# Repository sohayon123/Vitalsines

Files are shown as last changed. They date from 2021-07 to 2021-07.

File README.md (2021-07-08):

# Vitalsines
 
During my time as a co-op student at Vitalsines, I was responsible for the design and assembly of a variety of mechanical and electrical projects, however, the main project that I worked on was a device with the objective of measuring pulse wave velocity in a comfortable and easy way. 

## PCB Design
I developed 3 different PCBs for this project, one for filtering incoming data from piezo sensors of my design, one for aggregating sensor data lines, and one for sending this data to a DAQ. These PCBs were extremely small, at only 2cm diameter, and were assembled by hand. They contained a adjustable low pass filter to get rid of some of the noise in the analog signal from the piezo. The component size for this PCB was 0603 and the board was designed to have 4 layers, one ground plane and one 10V power plane, to help clean up the traces.

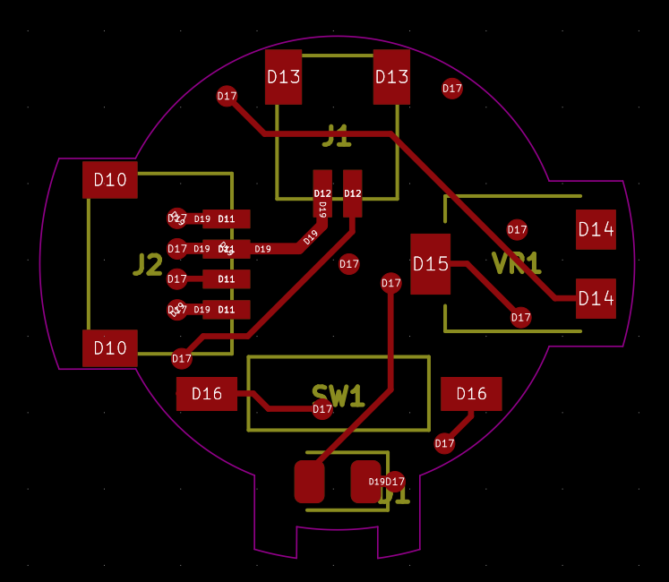
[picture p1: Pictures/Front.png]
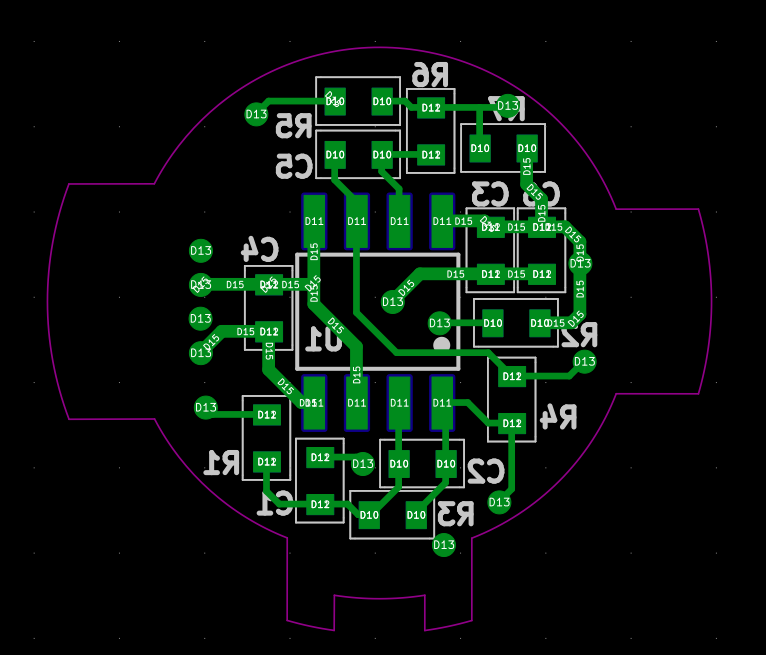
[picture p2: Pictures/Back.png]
  

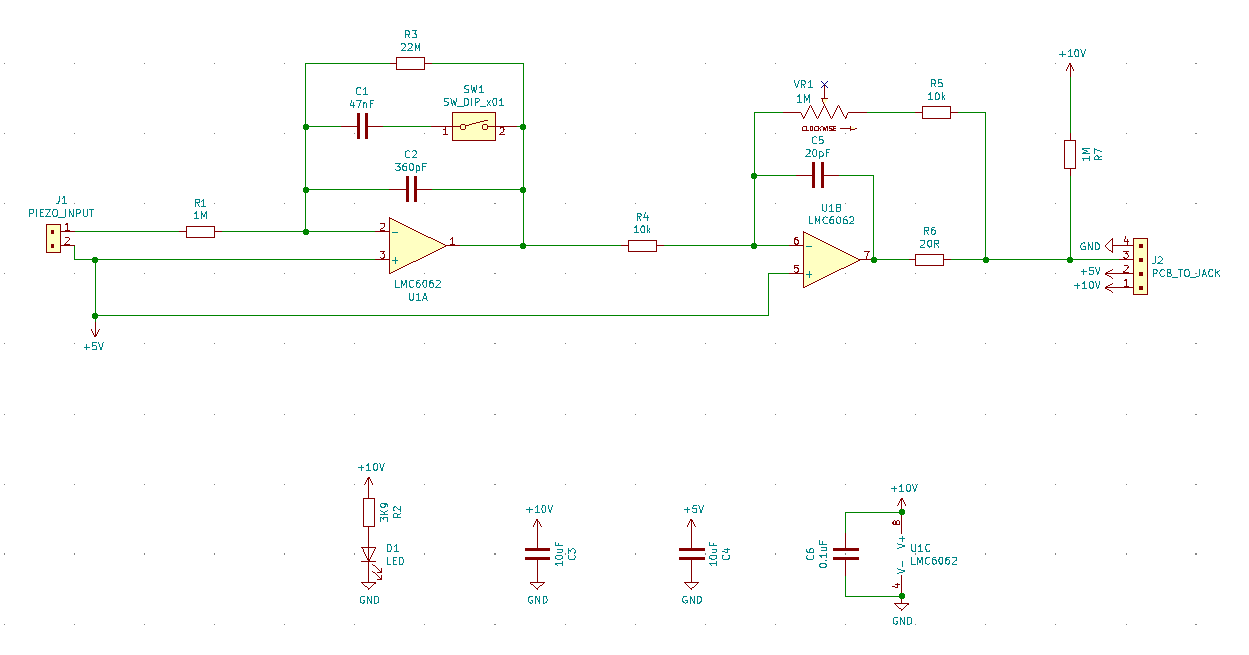
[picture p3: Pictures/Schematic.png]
 

## Mechanical Design

The mechanical design involved creating a strap that would host all of the electronics and sit comfortably on the chest. It also involved the design of some enclosures for the piezo sensors. Below are some pictures of the final result and some of the CAD files. The strap was designed with some areas of varying thickness to allow the PCBs to clip directly into the prototype strap. There were some cavities left in the strap as well to accomodate the various sensor cables.

  

[Link to Cad Viewer!](https://github.com/sohayon123/Vitalsines/blob/main/CAD/strap.STL)

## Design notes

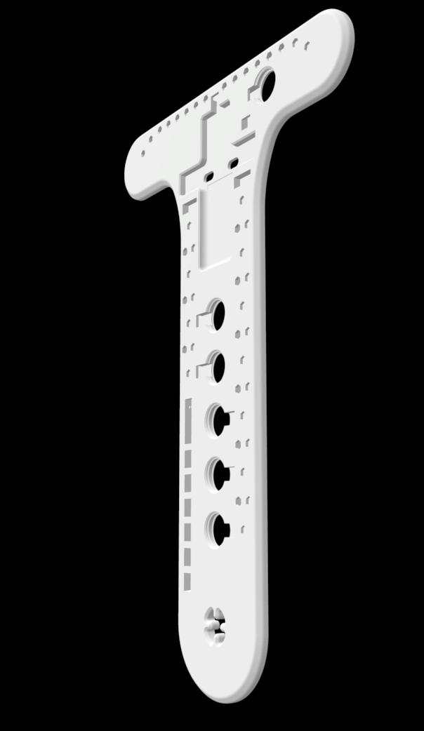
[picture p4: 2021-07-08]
Pictures/Chest Strap Render.png

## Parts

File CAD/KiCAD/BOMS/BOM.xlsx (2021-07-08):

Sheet: Piezo
Type | Units | Package | Value | Quantity | Annotations | DigiKey
Resistor | Ohms | 0603 | 1M | 2 | R1, R7 | A130109CT-ND
Resistor | Ohms | 0603 | 3K9 | 1 | R2 | RR08P3.9KDCT-ND
Resistor | Ohms | 0603 | 22M | 1 | R3 | 2019-RK73B1JTTD226JCT-ND
Resistor | Ohms | 0603 | 10K | 2 | R4, R5 | RR08P10.0KDCT-ND
Resistor | Ohms | 0603 | 20R | 1 | R6 | RNCP0603FTD20R0CT-ND
Capacitor | Farads | 0603 | 47n | 1 | C1 | 1276-1063-1-ND
Capacitor | Farads | 0603 | 360p | 1 | C2 | 478-10353-1-ND
Capacitor | Farads | 0603 | 10u | 2 | C3, C4 | 1276-6769-1-ND
Capacitor | Farads | 0603 | 20p | 1 | C5 | 1276-1187-1-ND
Capacitor | Farads | 0603 | 0.1u | 1 | C6 | 1276-CL10B104KB8NNNLCT-ND
LED |  | 0603 Diode | Green | 1 | D1 | 475-3118-1-ND
IC |  | SOIC-8 | LMC6062 | 1 | U1 | LMC6062IMX/NOPBCT-ND
Connector |  |  | Piezo Input | 1 | J1 | 455-1802-1-ND
Connector |  |  | Power Delivery and Data Out | 1 | J2 | 455-1804-1-ND
Switch |  |  |  | 1 | SW1 | 450-2546-1-ND
Potentiometer | Ohms |  |  | 1 | VR1 | 3314G-105ECT-ND
Jumper |  |  | 4 Pin, Reverse, 1ft | 1 |  | 455-3006-ND
Jumper |  |  | 2 Pin | 1 |  | 455-3005-ND

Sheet: Data Shield
Type | Units | Package | Value | Quantity | Annotations | DigiKey
Resistor | Ohms | 0805 | 5K23 | 6 | R1, R2, R3, R8, R9, R10 | 311-5.23KCRCT-ND
Resistor | Ohms | 0805 | 1K5 | 1 | R4 | A129751CT-ND
Resistor | Ohms | 0805 | 7K32 | 6 | R5, R6, R7, R11, R12, R13 | 311-7.32KCRCT-ND
Capacitor | Farads | 0805 | 4.7u/25V | 2 | C1, C8 | 1276-1244-1-ND
Capacitor | Farads | 0805 | 2n | 6 | C2, C3, C4, C10, C11, C12 | 1276-2471-1-ND
Capacitor | Farads | 0805 | 1n | 6 | C5, C6, C7, C14, C15, C16 | 1276-1020-1-ND
Capacitor | Farads | 0805 | 2.2u | 1 | C9 | 1276-1763-1-ND
Capacitor | Farads | 0805 | 1uF | 1 | C13 | 399-8004-1-ND
Polarized Capacitor | Farads | 6032-28 Kemet C | 47u/16V | 1 | C17 | 399-9739-1-ND
Polarized Capacitor | Farads | 1210 | 47u/10V | 1 | C18 | 478-3085-1-ND
Polarized Capacitor | Farads | 1206 | 10u/10V | 1 | C19 | 478-1654-1-ND
Capacitor | Farads | 0805 | 0.1u | 3 | C20, C21, C22 | 1276-1099-1-ND
IC |  | SOIC-8 | LMC6062 or TLV272IS | 3 | U1, U2, U4 | LMC6062IMX/NOPBCT-ND or TLV272IS-13DICT-ND
IC |  | SIP-7 | MDS01L-12 | 1 | U3 | 1866-3391-ND
IC |  | SOT-223-3 | MCP1804x-A002xDB | 1 | U5 | MCP1804T-A002I/DBCT-ND
IC |  | SOT-223-3 | MCP1804x-5002xDB | 1 | U6 | MCP1804T-5002I/DBCT-ND
IC |  | SOT-223-3 | MCP1804x-3302xDB | 1 | U9 | MCP1804T-3302I/DBCT-ND
Connector |  |  | 10 Pin Female Header Receptacle | 2 | U8, U10 | 732-2859-ND
Connector |  |  | D-sub 15 Female Connector THT | 1 | J1 | 626-1849-ND
LED |  | 0805 Diode | GREEN | 1 | D1 | 492-2525-1-ND
Inductor | Henrys | 1210 | 6.8u | 1 | L1 | 587-3032-1-ND

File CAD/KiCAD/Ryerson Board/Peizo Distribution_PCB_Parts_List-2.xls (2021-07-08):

 | Peizo Distribution PCB Parts List 15 Feb 2021
Item No | Supplier | Part Number | Type | Part | Qty | PCB Reference | 1 Off Price CAD | Qty Price CAD | Comments
1
2 | Digi-key | MCP1804T-A002I/DBCT-ND | SOT-223-3 | MCP1804T-A002I/DB | 1 | IC2 | CAD 1.05 | CAD 1.05
3 | Digi-key | MCP1804T-5002I/DBCT-ND | SOT-223-3 | MCP1804T-5002I/DB | 1 | IC3 | CAD 1.05 | CAD 1.05
4 | Digi-key | TLV272IS-13DICT-ND | SOIC8 | TLV272IS-13 | 4 | IC4,5,8,7 | CAD 0.87 | CAD 3.48
5 | Digi-key | 1866-3391-ND | SIL5 | MDS01L-12 | 1 | IC1 | CAD 7.86 | CAD 7.86
6
7 | Digi-key | 492-2525-1-ND | 0805 | Green LED | 1 | LD1 | CAD 0.75 | CAD 0.75
8
9 | Digi-key | 587-3032-2-ND | SMT | 6.8uH Inductor | 1 | L1 | CAD 0.35 | CAD 0.35
10
11 | Digi-key | 1276-1099-1-ND | 0805 | 0.1uF/25V Capacitor | 4 | C5,7,11,14 | CAD 0.14 | CAD 0.56
12 | Digi-key | 399-8004-1-ND | 0805 | 1uF/25V Capacitor | 1 | C1 | CAD 0.18 | CAD 0.18
13 | Digi-key | 1276-1020-1-ND | 0805 | 1nF/50V Capacitor | 8 | C19-26 | CAD 0.14 | CAD 1.12
14 | Digi-key | 1276-2471-1-ND | 0805 | 2nF/50V Capacitor | 8 | C6,8,9,10,12,13,15,16 | CAD 0.14 | CAD 1.12
15 | Digi-key | 1276-1763-2-ND | 0805 | 2.2uF/25V Capacitor | 1 | C17 | CAD 0.16 | CAD 0.16
16 | Digi-key | 1276-1248-1-ND | 0805 | 4.7uF/50V Capacitor | 2 | C4,18 | CAD 0.15 | CAD 0.30
17 | Digi-key | 399-8356-1-ND | Tant C | 47uF/16V Capacitor | 1 | C2 | CAD 1.25 | CAD 1.25
18 | Digi-key | 478-3085-1-ND | Tant B | 47uF/10V Capacitor | 1 | C3 | CAD 0.98 | CAD 0.98
19
20 | Digi-key | A129751CT-ND | 0805 | 1K5 Resistor | 1 | R1 | CAD 0.15 | CAD 0.15
21 | Digi-key | 311-5.23KCRCT-ND | 0805 | 5K23 Resistor | 8 | R10-17 | CAD 0.15 | CAD 1.20
22 | Digi-key | 311-7.32KCRCT-ND | 0805 | 7K32 Resistor | 8 | R2-9 | CAD 0.15 | CAD 1.20
23
24 | Digi-key | CP-43514SJCT-ND | SMT | 3.50mm 4 way Jack | 8 | J1-8 | CAD 1.50 | CAD 12.00
25 | Digi-key | S7053-ND | SIL20 | 20Way | 2 | J9,10 | CAD 1.77 | CAD 3.54 | 8.51mm Insulation Height
26
 |  |  |  |  |  |  | Total | CAD 38.30
 |  |  |  |  |  |  | TAX | CAD 0.00
 |  |  |  |  |  |  | Overall Total | CAD 38.30

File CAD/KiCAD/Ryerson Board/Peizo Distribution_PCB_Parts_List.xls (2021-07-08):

 | Peizo Distribution PCB Parts List 27 Jan 2021
Item No | Supplier | Part Number | Type | Part | Qty | PCB Reference | 1 Off Price CAD | Qty Price CAD | Comments
1
2 | Digi-key | MCP1804T-A002I/MTTR-ND | SOT89 | MCP1804T-A002I/MT | 1 | IC1 | CAD 1.05 | CAD 1.05
3 | Digi-key | MCP1804T-5002I/MTCT-ND | SOT89 | MCP1804T-5002I/MT | 1 | IC2 | CAD 1.05 | CAD 1.05
4 | Digi-key | TLV272IS-13DICT-ND | SOIC8 | TLV272IS-13 | 4 | IC3,4,5,6 | CAD 0.87 | CAD 3.48
5 | Digi-key | 1866-3391-ND | SIL5 | MDS01L-12 | 1 | IC7 | CAD 7.86 | CAD 7.86
6
7 | Digi-key | 1727-5229-1-ND | SOD-123W | 5V TVS | 1 | D1 | CAD 0.64 | CAD 0.64
8 | Digi-key | 492-2525-1-ND | 0805 | Green LED | 1 | LD1 | CAD 0.75 | CAD 0.75
9
10 | Digi-key | 587-3032-2-ND | SMT | 8.8uH Inductor | 1 | L1 | CAD 0.35 | CAD 0.35
11
12 | Digi-key | 1276-1099-1-ND | 0805 | 0.1uF/25V Capacitor | 4 | C21,22,23,24 | CAD 0.14 | CAD 0.56
13 | Digi-key | 399-8004-1-ND | 0805 | 1uF/25V Capacitor | 1 | C3 | CAD 0.18 | CAD 0.18
14 | Digi-key | 1276-1020-1-ND | 0805 | 1nF/50V Capacitor | 8 | C13-20 | CAD 0.14 | CAD 1.12
15 | Digi-key | 1276-2471-1-ND | 0805 | 2nF/50V Capacitor | 8 | C5-12 | CAD 0.14 | CAD 1.12
16 | Digi-key | 1276-1259-1-ND | 0805 | 4.7uF/10V Capacitor | 1 | C25 | CAD 0.14 | CAD 0.14
17 | Digi-key | 1276-1763-2-ND | 0805 | 2.2uF/25V Capacitor | 1 | C26 | CAD 0.16 | CAD 0.16
18 | Digi-key | 1276-1248-1-ND | 0805 | 4.7uF/50V Capacitor | 2 | C1,25 | CAD 0.15 | CAD 0.30
19 | Digi-key | 399-8356-1-ND | Tant C | 47uF/16V Capacitor | 1 | C2 | CAD 1.25 | CAD 1.25
20 | Digi-key | 478-3085-1-ND | Tant B | 47uF/10V Capacitor | 1 | C4 | CAD 0.98 | CAD 0.98
21
22 | Digi-key | A129751CT-ND | 0805 | 1K5 Resistor | 1 | R1 | CAD 0.15 | CAD 0.15
23 | Digi-key | 311-5.23KCRCT-ND | 0805 | 5K23 Resistor | 8 | R2-9 | CAD 0.15 | CAD 1.20
24 | Digi-key | 311-7.32KCRCT-ND | 0805 | 7K32 Resistor | 8 | R10-17 | CAD 0.15 | CAD 1.20
25
26 | Digi-key | 2073-USB3090-30-ACT-ND | PTH | Micro USB | 1 | J1 | CAD 0.95 | CAD 0.95
27 | Digi-key | CP-43514SJCT-ND | SMT | 3.50mm 4 way Jack | 8 | J2-9 | CAD 1.50 | CAD 12.00
28 | Digi-key | S7053-ND | SIL20 | 20Way | 2 | J10,11 | CAD 1.77 | CAD 3.54
29 | Digi-key | 839-1039-ND | Cable Assy | Cable Assy with mono 3.5mm plug | 8 | J10-17 | CAD 4.53 | CAD 36.24
30
 |  |  |  |  |  |  | Total | CAD 76.27
 |  |  |  |  |  |  | TAX | CAD 0.00
 |  |  |  |  |  |  | Overall Total | CAD 76.27

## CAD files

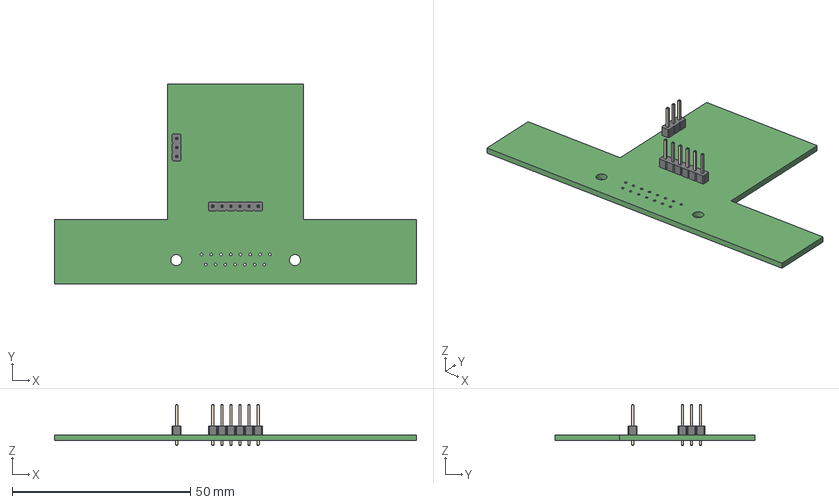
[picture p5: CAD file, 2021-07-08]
CAD/KiCAD/Sensor Data Collection Board/Sensor Data Collection Board.step
101.6 x 56.2 x 11.5 mm

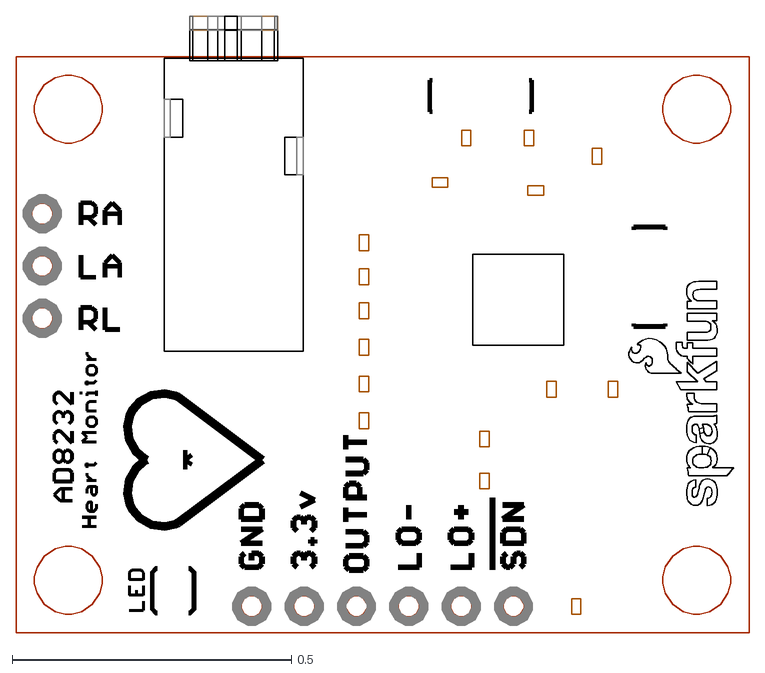
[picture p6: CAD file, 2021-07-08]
CAD/KiCAD/Sensor Data Collection Board/sparkfun_sensors_ad8232_breadboard.dxf
1.31 x 1.10

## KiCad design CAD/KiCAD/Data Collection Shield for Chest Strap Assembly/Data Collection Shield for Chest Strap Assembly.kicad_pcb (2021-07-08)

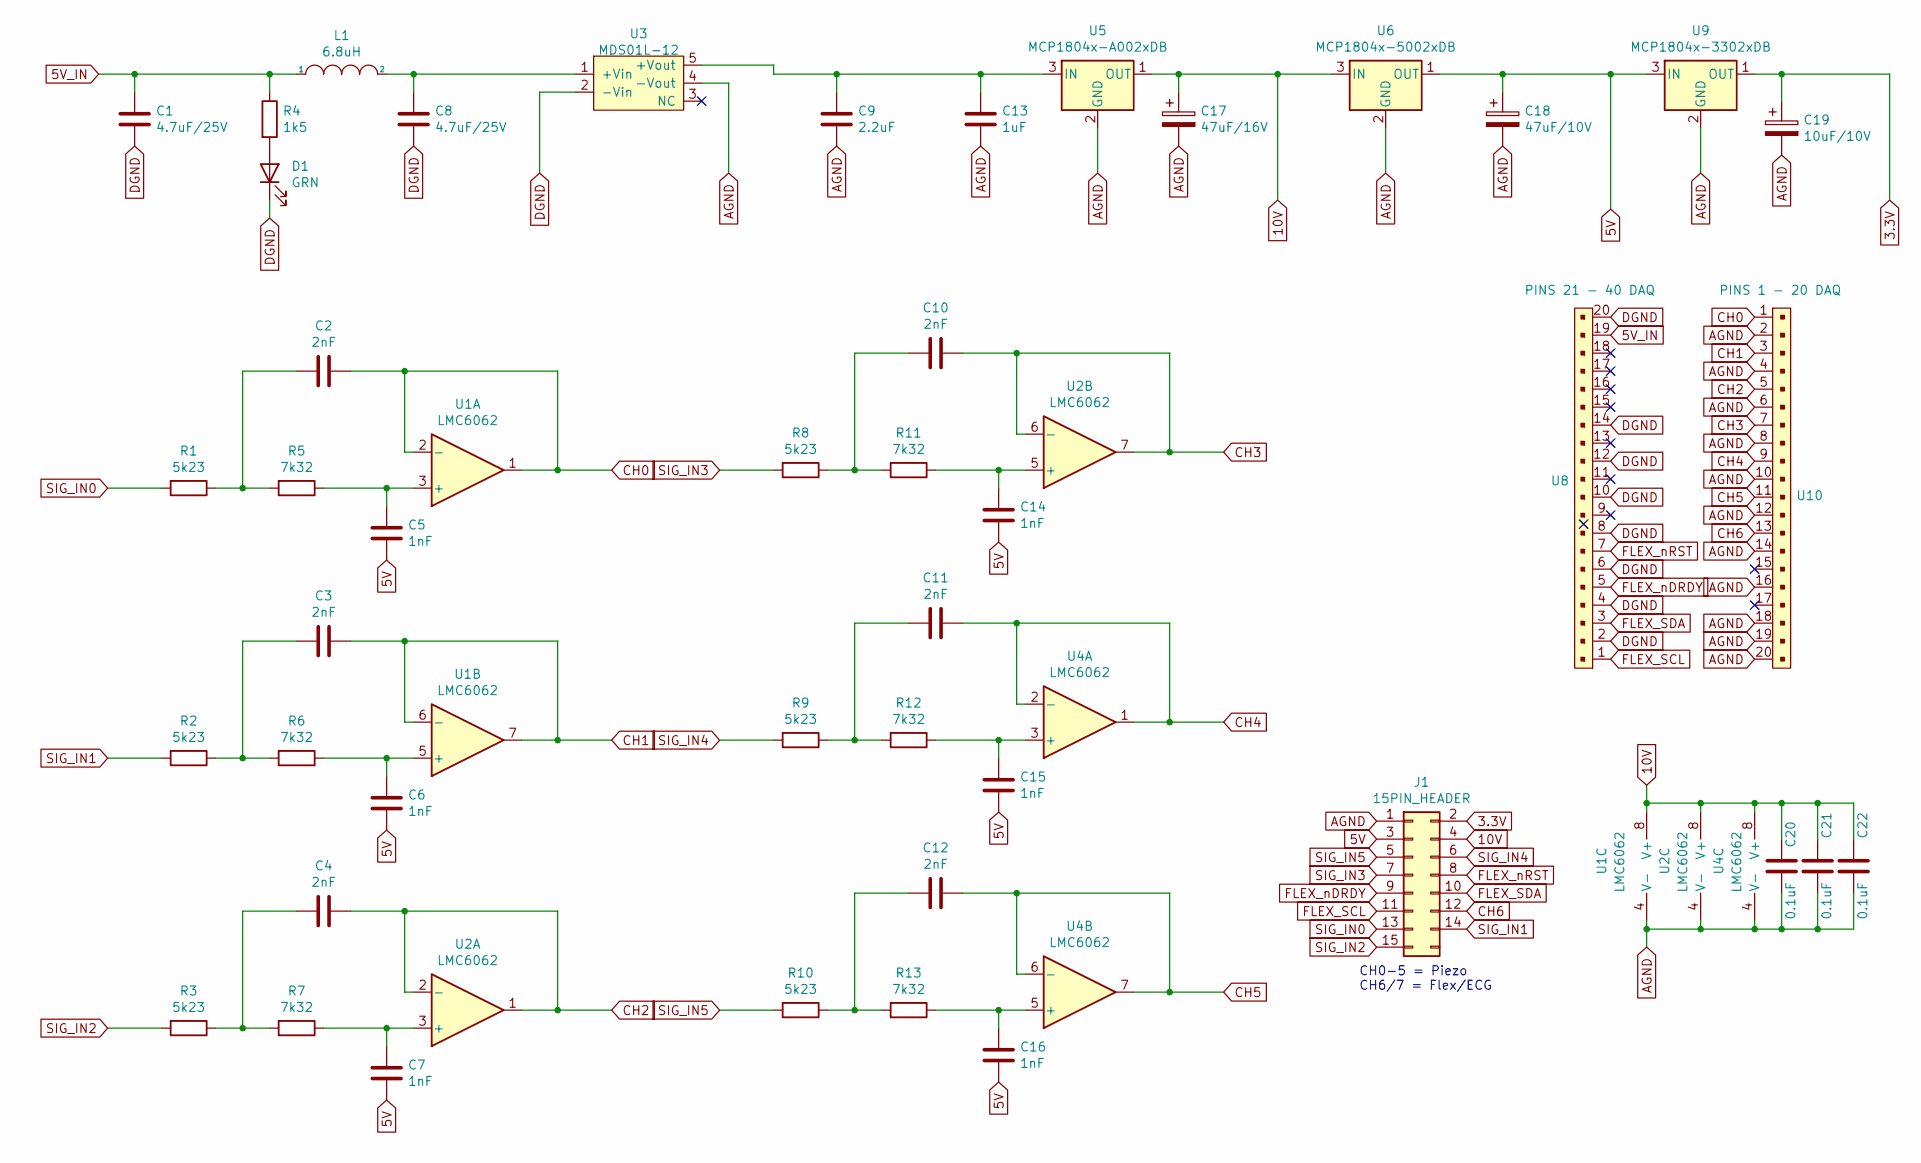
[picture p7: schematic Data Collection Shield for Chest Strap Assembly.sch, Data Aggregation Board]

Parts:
C1, C8: 4.7uF/25V; 0805
C2, C3, C4, C10, C11, C12: 2nF; 0805
C5, C6, C7, C14, C15, C16: 1nF; 0805
C9: 2.2uF; 0805
C13: 1uF; 0805
C17: 47uF/16V; CP_EIA-6032-28_Kemet-C
C18: 47uF/10V; 1210
C19: 10uF/10V; 1206
C20, C21, C22: 0.1uF; 0805
D1: GRN; 0805
J1: 15PIN_HEADER; DB15 2 row
L1: 6.8uH; 1210
R1, R2, R3, R8, R9, R10: 5k23; 0805
R4: 1k5; 0805
R5, R6, R7, R11, R12, R13: 7k32; 0805
U1, U2, U4: LMC6062; LMC6062IMX
U3: MDS01L-12; SIP-7
U5: MCP1804x-A002xDB; SOT-223-3_TabPin2
U6: MCP1804x-5002xDB; SOT-223-3_TabPin2
U8: PINS 21 - 40 DAQ; PinSocket_1x20_P2.54mm_Vertical
U9: MCP1804x-3302xDB; SOT-223-3_TabPin2
U10: PINS 1 - 20 DAQ; PinSocket_1x20_P2.54mm_Vertical

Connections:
3.3V: C19.1, J1.2, U9.1 (OUT)
5V: C5.2, C6.2, C7.2, C14.2, C15.2, C16.2, C18.1, J1.3, U6.1 (OUT), U9.3 (IN)
5V_IN: C1.1, L1.1, R4.1, U8.19
10V: C17.1, C20.1, C21.1, C22.1, J1.4, U1.8 (V+), U2.8 (V+), U4.8 (V+), U5.1 (OUT), U6.3 (IN)
AGND: C9.2, C13.2, C17.2, C18.2, C19.2, C20.2, C21.2, C22.2, J1.1, U1.4 (V-), U2.4 (V-), U3.4 (-Vout), U4.4 (V-), U5.2 (GND), U6.2 (GND), U9.2 (GND), U10.2, U10.4, U10.6, U10.8, U10.10, U10.12, U10.14, U10.16, U10.18, U10.19, U10.20
CH0: C2.1, U1.1, U1.2 (-), U10.1
CH1: C3.1, U1.6 (-), U1.7, U10.3
CH2: C4.1, U2.1, U2.2 (-), U10.5
CH3: C10.1, U2.6 (-), U2.7, U10.7
CH4: C11.1, U4.1, U4.2 (-), U10.9
CH5: C12.1, U4.6 (-), U4.7, U10.11
CH6: J1.12, U10.13
DGND: C1.2, C8.2, D1.1 (K), U3.2 (-Vin), U8.2, U8.4, U8.6, U8.8, U8.10, U8.12, U8.14, U8.20
FLEX_SCL: J1.11, U8.1
FLEX_SDA: J1.10, U8.3
FLEX_nDRDY: J1.9, U8.5
FLEX_nRST: J1.8, U8.7
unnamed: C2.2, R1.1, R5.2
unnamed: C3.2, R2.1, R6.2
unnamed: C4.2, R3.1, R7.2
unnamed: C5.1, R5.1, U1.3 (+)
unnamed: C6.1, R6.1, U1.5 (+)
unnamed: C7.1, R7.1, U2.3 (+)
unnamed: C8.1, L1.2, U3.1 (+Vin)
unnamed: C10.2, R8.1, R11.2
unnamed: C11.2, R9.1, R12.2
unnamed: C12.2, R10.1, R13.2
unnamed: C9.1, C13.1, U3.5 (+Vout), U5.3 (IN)
unnamed: C14.1, R11.1, U2.5 (+)
unnamed: C15.1, R12.1, U4.3 (+)
unnamed: C16.1, R13.1, U4.5 (+)
unnamed: D1.2 (A), R4.2
SIG_IN0: J1.13, R1.2
SIG_IN1: J1.14, R2.2
SIG_IN2: J1.15, R3.2
SIG_IN3: J1.7, R8.2
SIG_IN4: J1.6, R9.2
SIG_IN5: J1.5, R10.2

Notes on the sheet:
CH0-5 = Piezo CH6/7 = Flex/ECG

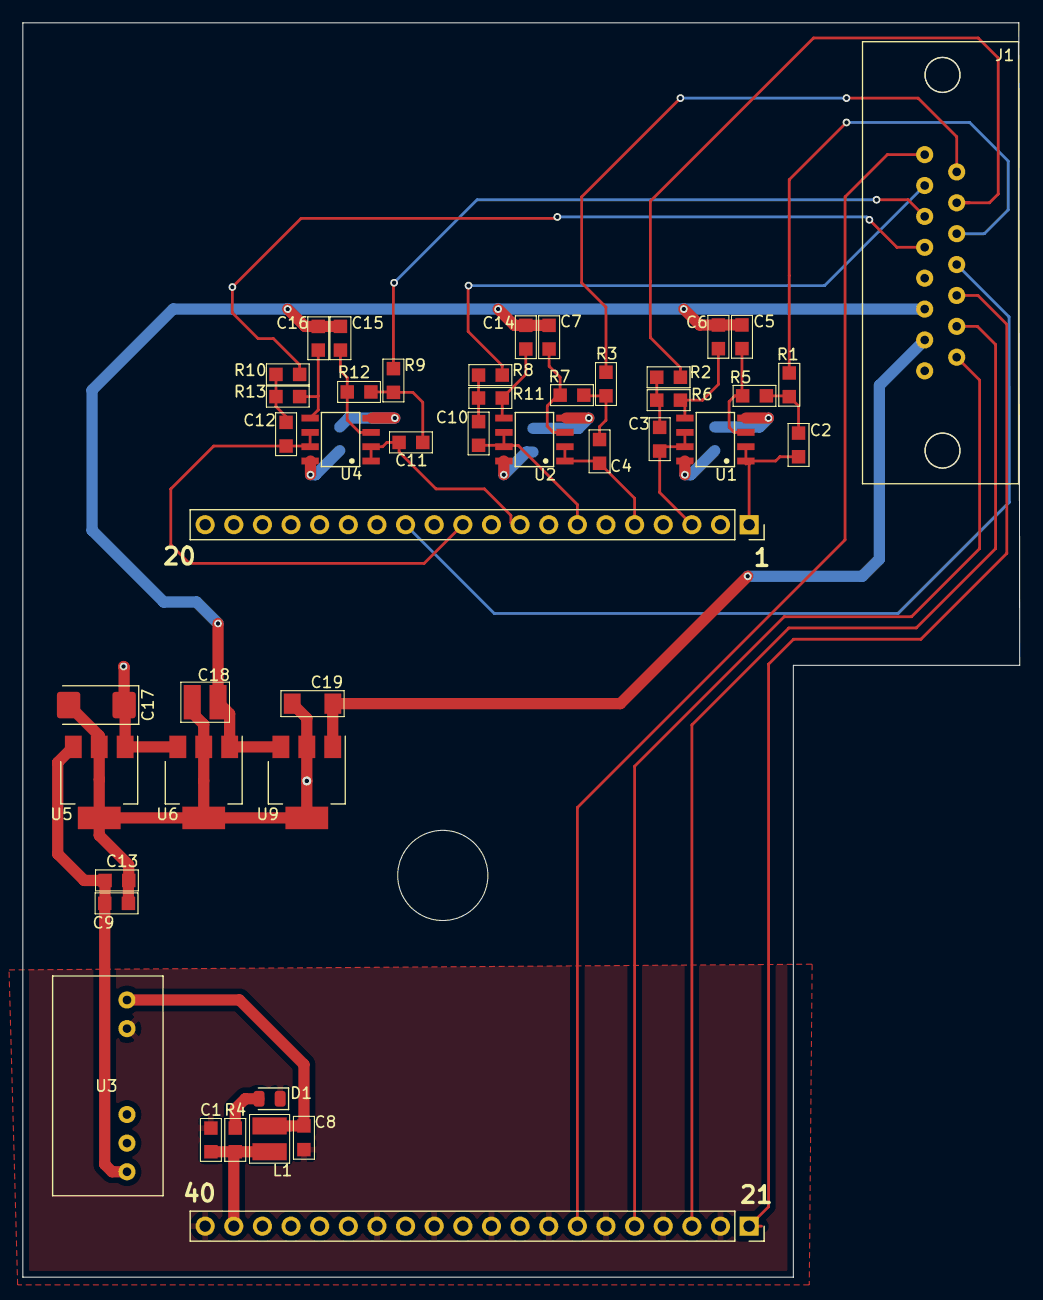
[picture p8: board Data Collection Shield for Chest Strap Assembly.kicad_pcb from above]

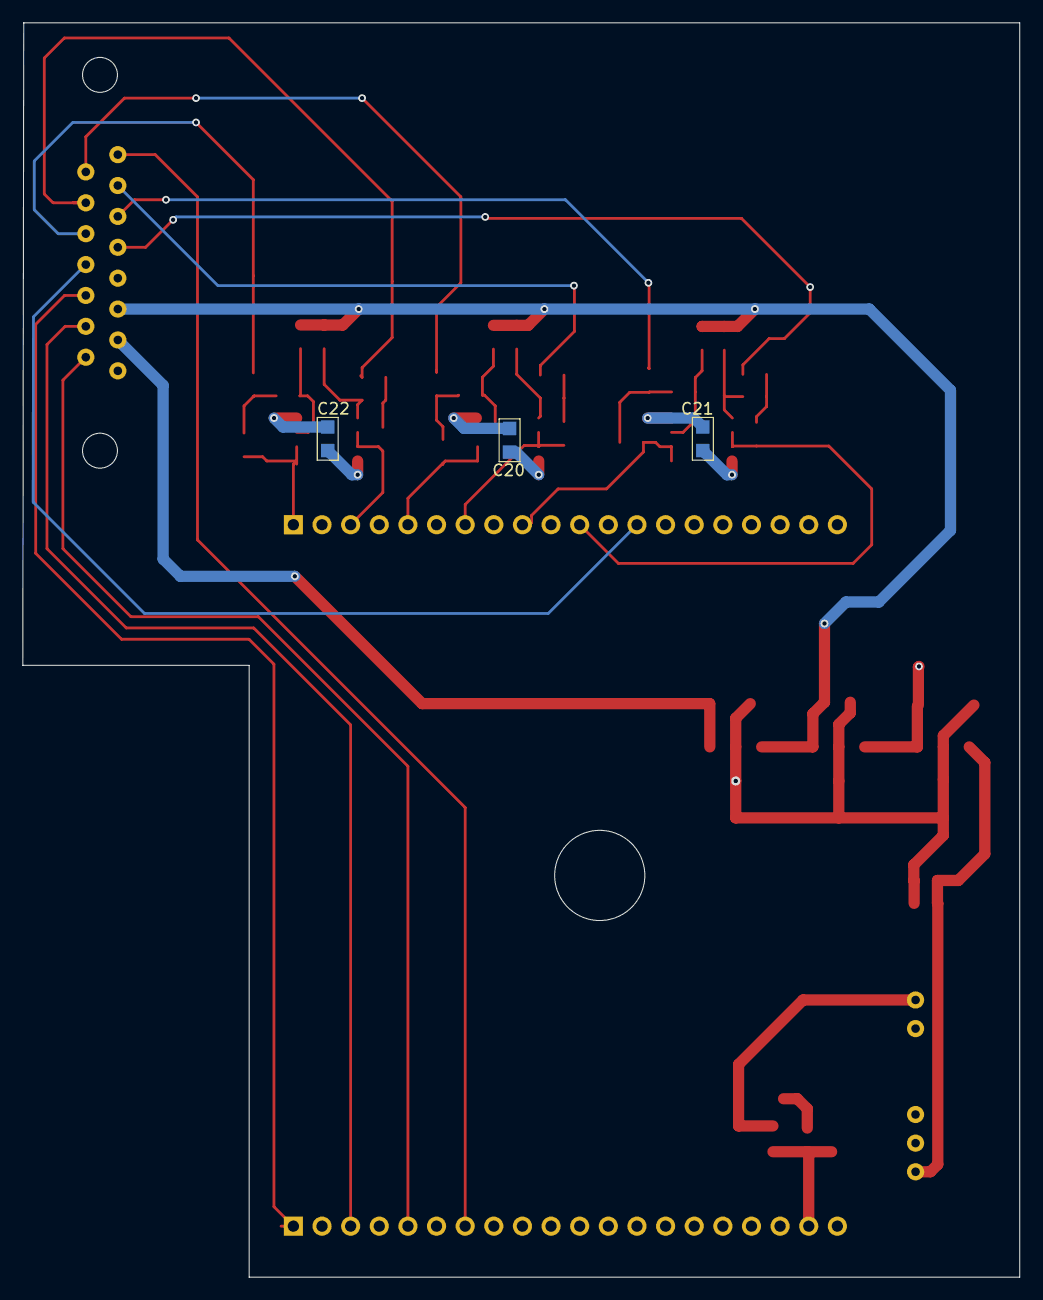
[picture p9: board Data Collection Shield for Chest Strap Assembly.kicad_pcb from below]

Board: 4 copper layers, 88.4 x 111.3 mm, 47 parts (3 on the bottom side), 38 nets.

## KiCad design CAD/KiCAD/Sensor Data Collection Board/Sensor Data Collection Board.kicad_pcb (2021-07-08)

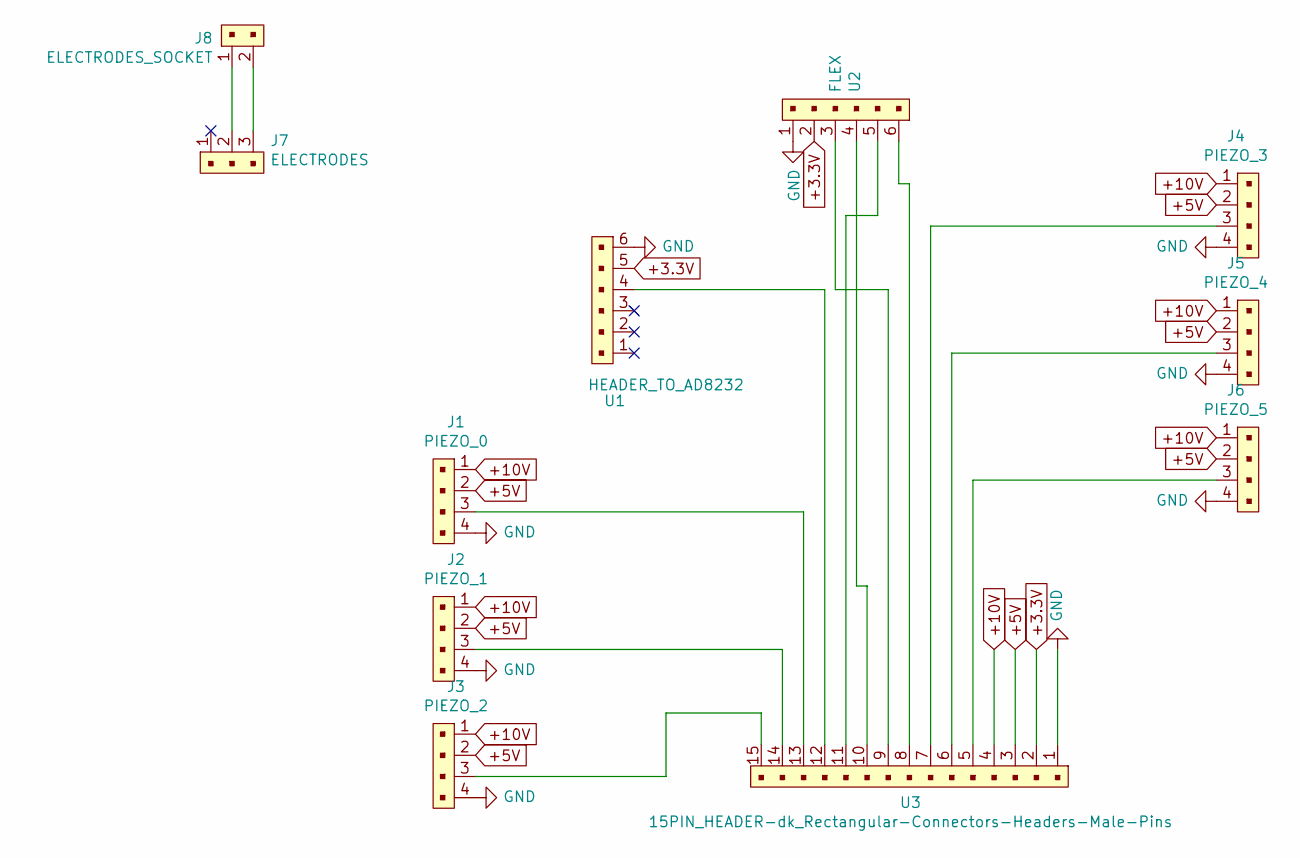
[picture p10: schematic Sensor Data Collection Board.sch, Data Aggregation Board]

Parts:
J1: PIEZO_0; BM04B-SRSS-TB; MPN B4B-PH-K-S(LF)(SN); Digi-Key_PN 455-1706-ND
J2: PIEZO_1; BM04B-SRSS-TB; MPN B4B-PH-K-S(LF)(SN); Digi-Key_PN 455-1706-ND
J3: PIEZO_2; BM04B-SRSS-TB; MPN B4B-PH-K-S(LF)(SN); Digi-Key_PN 455-1706-ND
J4: PIEZO_3; BM04B-SRSS-TB; MPN B4B-PH-K-S(LF)(SN); Digi-Key_PN 455-1706-ND
J5: PIEZO_4; BM04B-SRSS-TB; MPN B4B-PH-K-S(LF)(SN); Digi-Key_PN 455-1706-ND
J6: PIEZO_5; BM04B-SRSS-TB; MPN B4B-PH-K-S(LF)(SN); Digi-Key_PN 455-1706-ND
J7: ELECTRODES; PinHeader_1x03_P2.54mm_Vertical; MPN 640456-3; Digi-Key_PN A19470-ND
J8: ELECTRODES_SOCKET; SM02B-SRSS-TB; MPN 22-23-2021; Digi-Key_PN WM4200-ND
U1: HEADER_TO_AD8232; PinHeader_1x06_P2.54mm_Vertical
U2: FLEX; BM06B-SRSS-TB
U3: 15PIN_HEADER-dk_Rectangular-Connectors-Headers-Ma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; DB15 2 row

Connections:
+3.3V: U1.5, U2.2, U3.2
+5V: J1.2, J2.2, J3.2, J4.2, J5.2, J6.2, U3.3
+10V: J1.1, J2.1, J3.1, J4.1, J5.1, J6.1, U3.4
GND: J1.4, J2.4, J3.4, J4.4, J5.4, J6.4, U1.6, U2.1, U3.1
unnamed: J1.3, U3.13
unnamed: J2.3, U3.14
unnamed: J3.3, U3.15
unnamed: J4.3, U3.7
unnamed: J5.3, U3.6
unnamed: J6.3, U3.5
unnamed: J7.2, J8.1
unnamed: J7.3, J8.2
unnamed: U1.4, U3.12
unnamed: U2.3, U3.9
unnamed: U2.4, U3.10
unnamed: U2.5, U3.11
unnamed: U2.6, U3.8

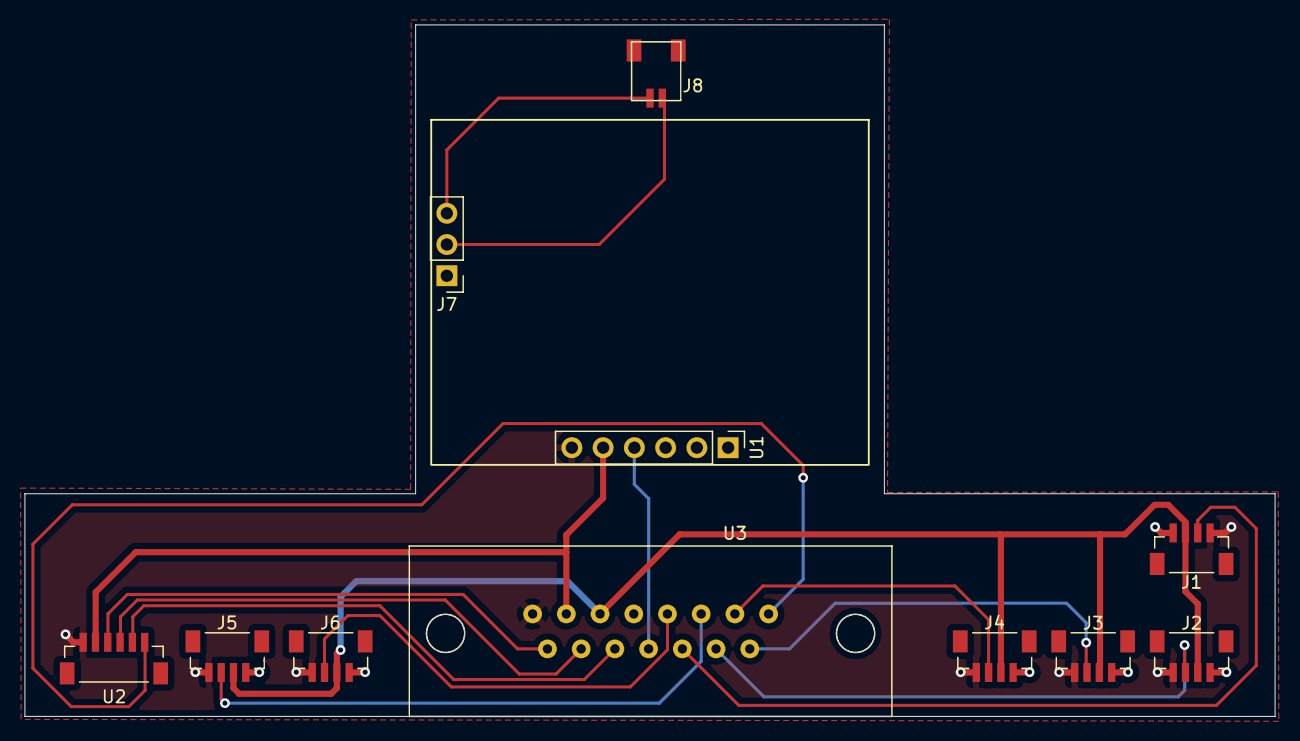
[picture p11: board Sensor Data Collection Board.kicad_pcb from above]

Board: 4 copper layers, 101.6 x 56.2 mm, 11 parts (0 on the bottom side), 17 nets.

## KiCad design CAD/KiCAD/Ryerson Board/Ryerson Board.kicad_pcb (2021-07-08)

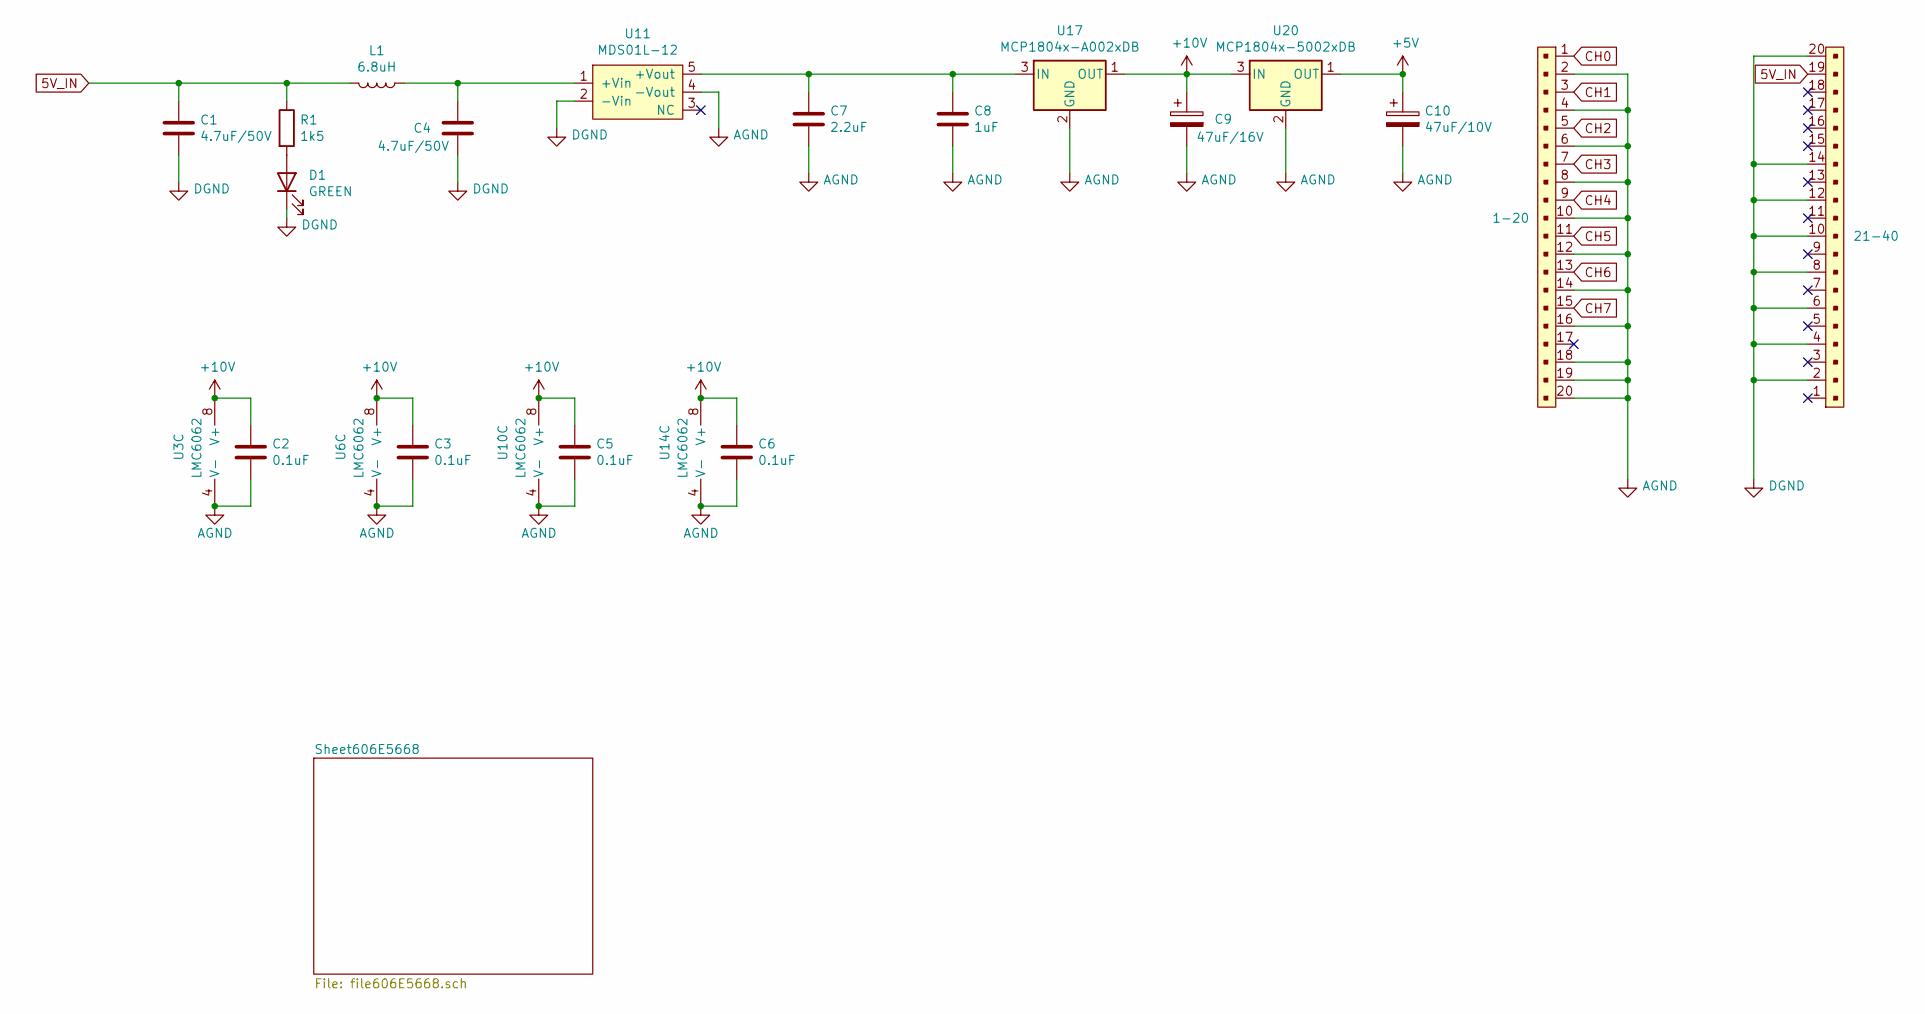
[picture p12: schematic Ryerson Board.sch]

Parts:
C1, C4: 4.7uF/50V; 0805
C2, C3, C5, C6: 0.1uF; 0805
C7: 2.2uF; 0805
C8: 1uF; 0805
C9: 47uF/16V; CP_EIA-6032-28_Kemet-C
C10: 47uF/10V; 1210
D1: GREEN; LED_0805_2012Metric_Pad1.15x1.40mm_HandSolder
L1: 6.8uH; 1210
R1: 1k5; 0805
U3, U6, U10, U14: LMC6062; LMC6062IMX
U11: MDS01L-12; SIP-7
U17: MCP1804x-A002xDB; SOT-223-3_TabPin2
U20: MCP1804x-5002xDB; SOT-223-3_TabPin2
U23: 1-20; PinSocket_1x20_P2.54mm_Vertical
U26: 21-40; PinSocket_1x20_P2.54mm_Vertical

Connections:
5V_IN: C1.1, L1.2, R1.1, U26.19
+5V: C10.1, U20.1 (OUT); also elsewhere on the board
+10V: C2.1, C3.1, C5.1, C6.1, C9.1, U3.8 (V+), U6.8 (V+), U10.8 (V+), U14.8 (V+), U17.1 (OUT), U20.3 (IN); also elsewhere on the board
AGND: C2.2, C3.2, C5.2, C6.2, C7.2, C8.2, C9.2, C10.2, U3.4 (V-), U6.4 (V-), U10.4 (V-), U11.4 (-Vout), U14.4 (V-), U17.2 (GND), U20.2 (GND), U23.2, U23.4, U23.6, U23.8, U23.10, U23.12, U23.14, U23.16, U23.18, U23.19, U23.20; also elsewhere on the board
CH0: U23.1; also elsewhere on the board
CH1: U23.3; also elsewhere on the board
CH2: U23.5; also elsewhere on the board
CH3: U23.7; also elsewhere on the board
CH4: U23.9; also elsewhere on the board
CH5: U23.11; also elsewhere on the board
CH6: U23.13; also elsewhere on the board
CH7: U23.15; also elsewhere on the board
DGND: C1.2, C4.2, D1.1 (K), U11.2 (-Vin), U26.2, U26.4, U26.6, U26.8, U26.10, U26.12, U26.14, U26.20
unnamed: C4.1, L1.1, U11.1 (+Vin)
unnamed: C7.1, C8.1, U11.5 (+Vout), U17.3 (IN)
unnamed: D1.2 (A), R1.2

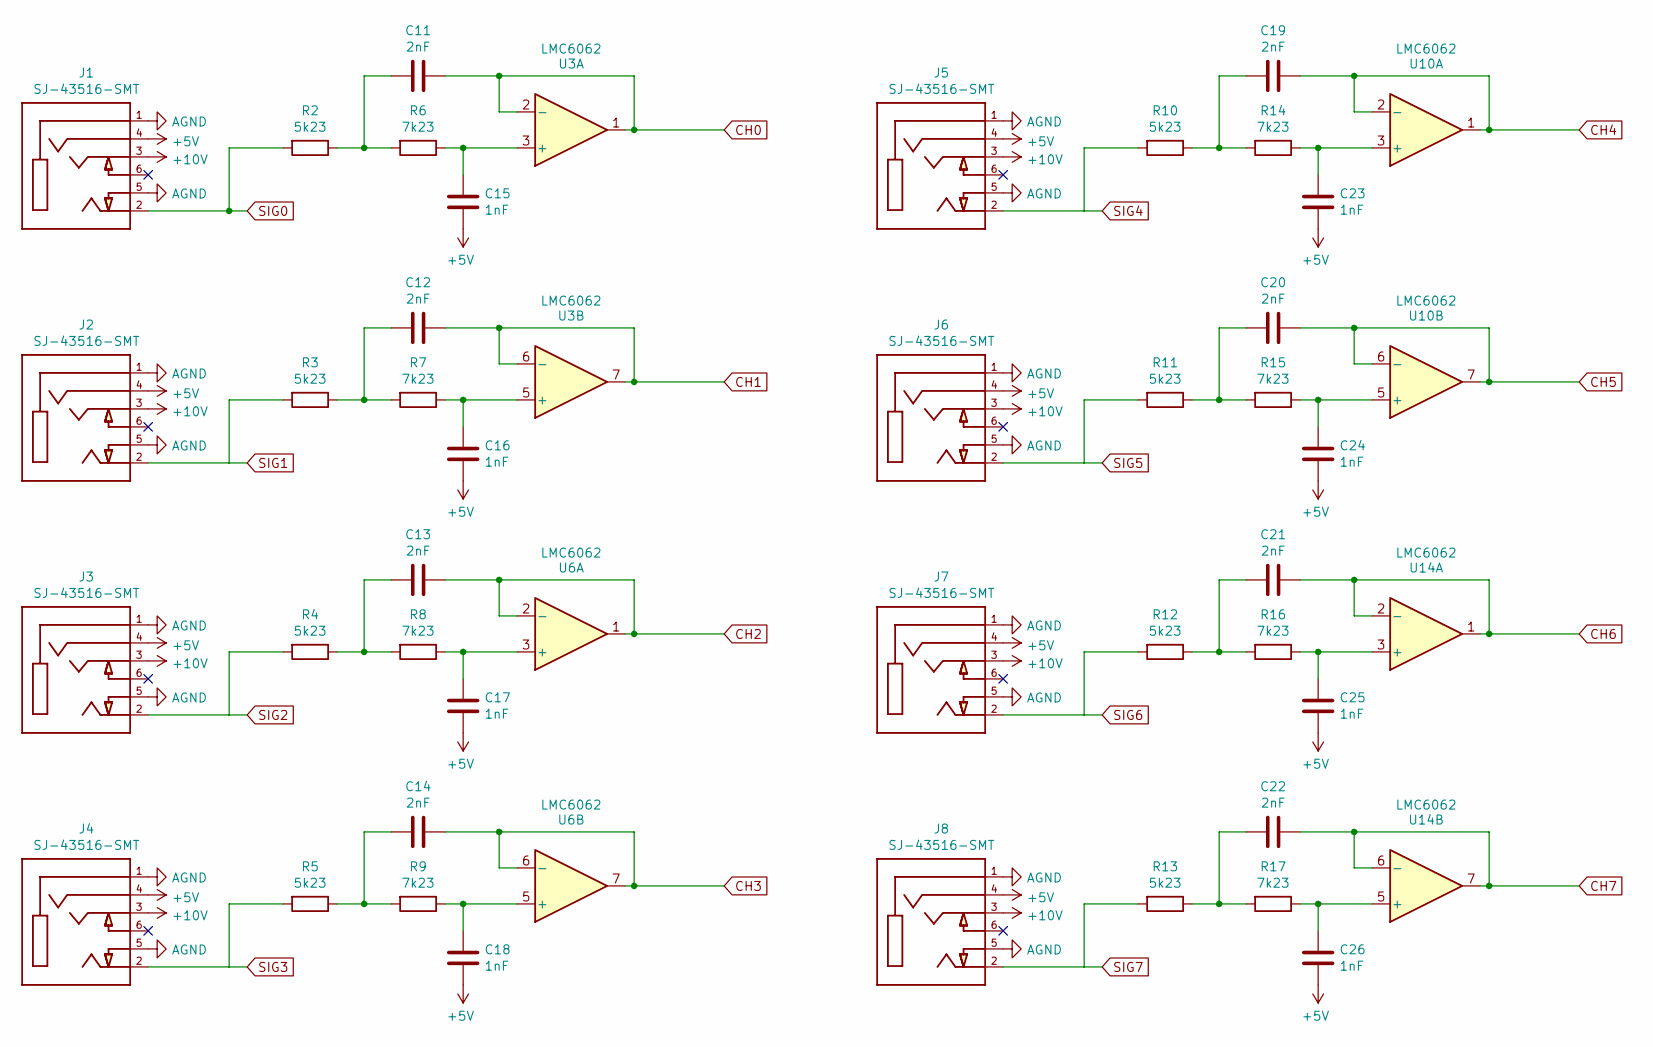
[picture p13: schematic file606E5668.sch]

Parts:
C11, C12, C13, C14, C19, C20, C21, C22: 2nF; 0805
C15, C16, C17, C18, C23, C24, C25, C26: 1nF; 0805
J1, J2, J3, J4, J5, J6, J7, J8: SJ-43516-SMT; CUI_SJ-43516-SMT; PART_REV 1.02
R2, R3, R4, R5, R10, R11, R12, R13: 5k23; 0805
R6, R7, R8, R9, R14, R15, R16, R17: 7k23; 0805
U3, U6, U10, U14: LMC6062; LMC6062IMX

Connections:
+5V: C15.2, C16.2, C17.2, C18.2, C23.2, C24.2, C25.2, C26.2, J1.4, J2.4, J3.4, J4.4, J5.4, J6.4, J7.4, J8.4; also elsewhere on the board
+10V: J1.3, J2.3, J3.3, J4.3, J5.3, J6.3, J7.3, J8.3; also elsewhere on the board
AGND: J1.1, J1.5, J2.1, J2.5, J3.1, J3.5, J4.1, J4.5, J5.1, J5.5, J6.1, J6.5, J7.1, J7.5, J8.1, J8.5; also elsewhere on the board
CH0: C11.1, U3.1, U3.2 (-); also elsewhere on the board
CH1: C12.1, U3.6 (-), U3.7; also elsewhere on the board
CH2: C13.1, U6.1, U6.2 (-); also elsewhere on the board
CH3: C14.1, U6.6 (-), U6.7; also elsewhere on the board
CH4: C19.1, U10.1, U10.2 (-); also elsewhere on the board
CH5: C20.1, U10.6 (-), U10.7; also elsewhere on the board
CH6: C21.1, U14.1, U14.2 (-); also elsewhere on the board
CH7: C22.1, U14.6 (-), U14.7; also elsewhere on the board
unnamed: C11.2, R2.1, R6.2
unnamed: C12.2, R3.1, R7.2
unnamed: C13.2, R4.1, R8.2
unnamed: C14.2, R5.1, R9.2
unnamed: C15.1, R6.1, U3.3 (+)
unnamed: C16.1, R7.1, U3.5 (+)
unnamed: C17.1, R8.1, U6.3 (+)
unnamed: C18.1, R9.1, U6.5 (+)
unnamed: C19.2, R10.1, R14.2
unnamed: C20.2, R11.1, R15.2
unnamed: C21.2, R12.1, R16.2
unnamed: C22.2, R13.1, R17.2
unnamed: C23.1, R14.1, U10.3 (+)
unnamed: C24.1, R15.1, U10.5 (+)
unnamed: C25.1, R16.1, U14.3 (+)
unnamed: C26.1, R17.1, U14.5 (+)
unnamed: J1.2, R2.2
unnamed: J2.2, R3.2
unnamed: J3.2, R4.2
unnamed: J4.2, R5.2
unnamed: J5.2, R10.2
unnamed: J6.2, R11.2
unnamed: J7.2, R12.2
unnamed: J8.2, R13.2

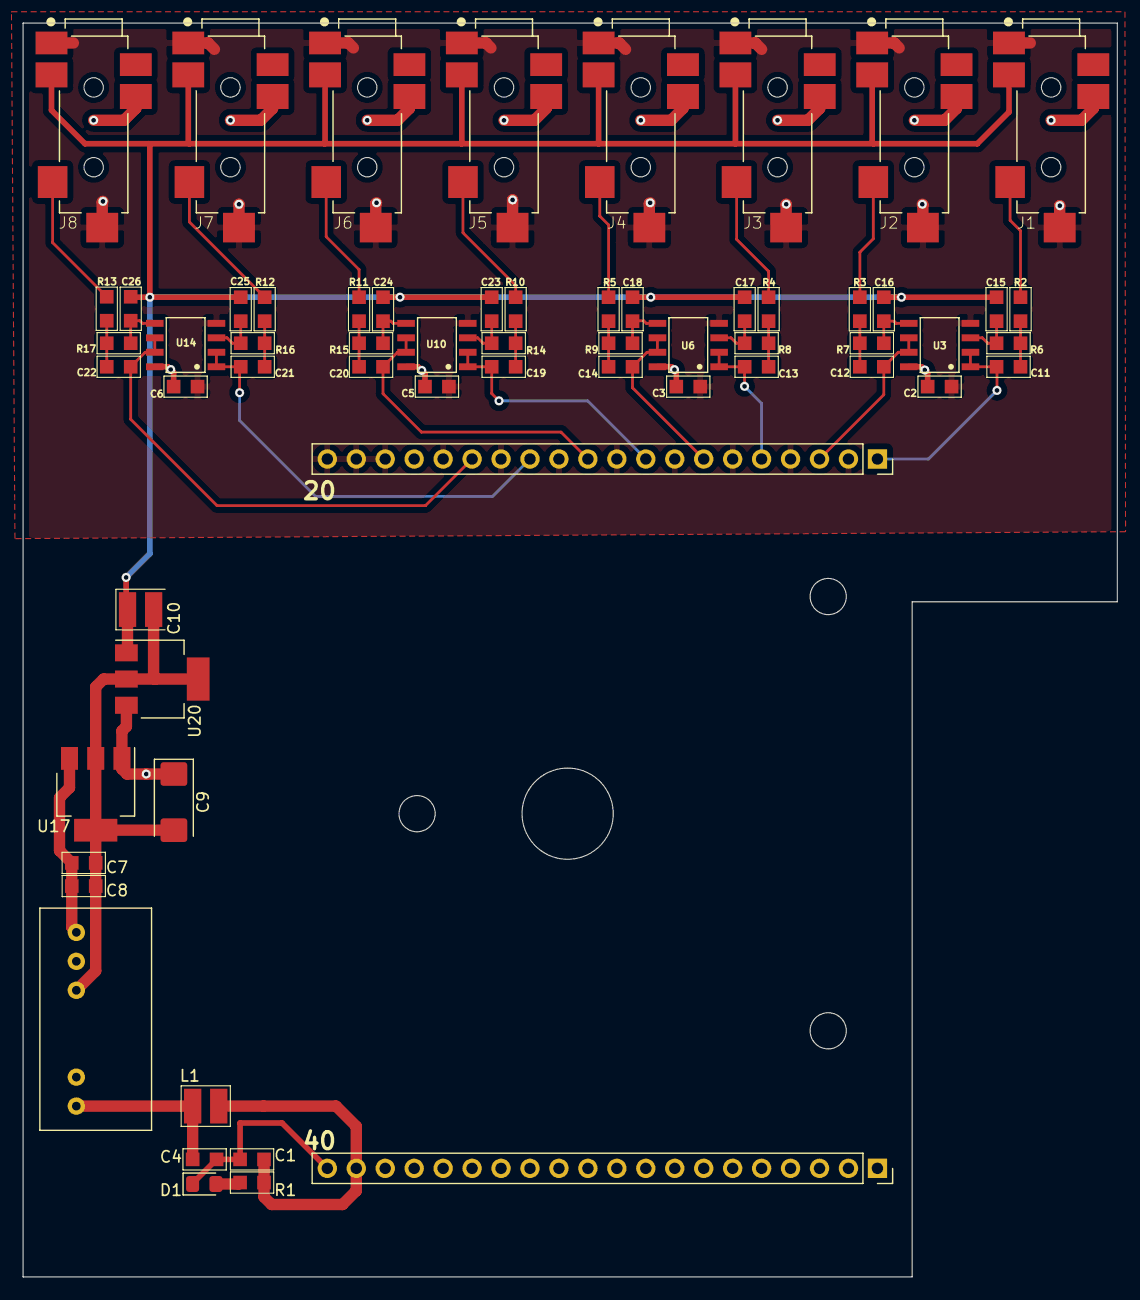
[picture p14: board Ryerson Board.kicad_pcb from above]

Board: 4 copper layers, 96.0 x 110.0 mm, 62 parts (0 on the bottom side), 40 nets.

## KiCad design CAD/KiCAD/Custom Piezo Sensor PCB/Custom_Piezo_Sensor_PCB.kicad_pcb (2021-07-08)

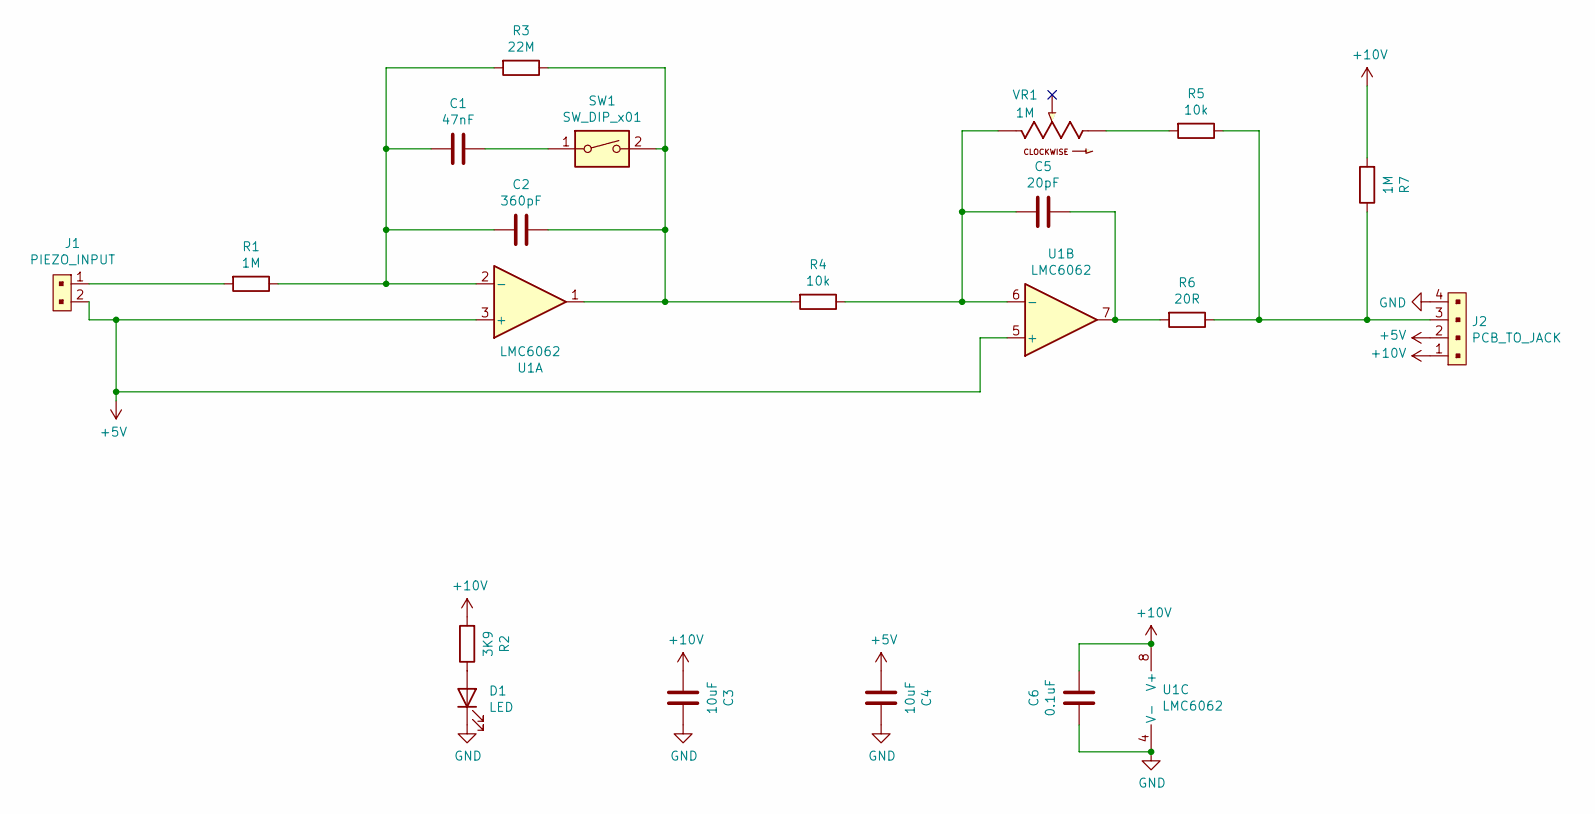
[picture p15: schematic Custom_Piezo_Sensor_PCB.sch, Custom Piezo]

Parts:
C1: 47nF; 0603
C2: 360pF; 0603
C3, C4: 10uF; 0603
C5: 20pF; 0603
C6: 0.1uF; 0603
D1: LED; 0603
J1: PIEZO_INPUT; SM02B-SRSS-TB; MPN S2B-PH-SM4-TB(LF)(SN); Digi-Key_PN 455-1749-1-ND
J2: PCB_TO_JACK; SM04B-SRSS-TB; MPN B4B-PH-K-S(LF)(SN); Digi-Key_PN 455-1706-ND
R1, R7: 1M; 0603
R2: 3K9; 0603
R3: 22M; 0603
R4, R5: 10k; 0603
R6: 20R; 0603
SW1: SW_DIP_x01; EDS01SGNNTR04Q
U1: LMC6062; LMC6062IMX
VR1: 1M; 3314G-1-105E; PARTREV 08/19

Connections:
+5V: C4.2, J1.2, J2.2, U1.3 (+), U1.5 (+)
+10V: C3.2, C6.1, J2.1, R2.2, R7.2, U1.8 (V+)
GND: C3.1, C4.1, C6.2, D1.1 (K), J2.4, U1.4 (V-)
unnamed: C1.1, SW1.1
unnamed: C1.2, C2.2, R1.1, R3.2, U1.2 (-)
unnamed: C2.1, R3.1, R4.2, SW1.2, U1.1
unnamed: C5.1, R6.2, U1.7
unnamed: C5.2, R4.1, U1.6 (-), VR1.1
unnamed: D1.2 (A), R2.1
unnamed: J1.1, R1.2
unnamed: J2.3, R5.1, R6.1, R7.1
unnamed: R5.2, VR1.3

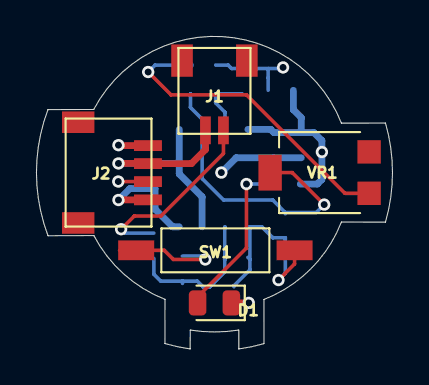
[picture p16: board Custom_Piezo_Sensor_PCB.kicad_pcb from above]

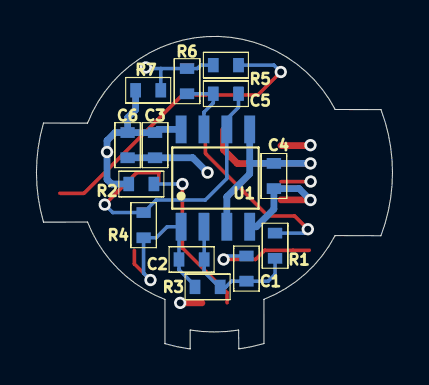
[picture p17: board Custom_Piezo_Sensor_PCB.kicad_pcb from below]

Board: 4 copper layers, 19.8 x 17.4 mm, 19 parts (14 on the bottom side), 12 nets.
